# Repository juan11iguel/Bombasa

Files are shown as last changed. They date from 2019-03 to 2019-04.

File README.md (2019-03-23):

# Bombasa
En este proyecto intentamos implementar un arduino, con un driver para un motor DC y, haciendo uso de periféricos como una pantalla de 4 dígitos y 7 segmentos, así como de botones, interruptores, etc. Establecer dos modos de funcionamiento en un sistema cuyo objetivo es el impulso de reactivos químicos para mezcla de componentes (bomba PERISTÁLTICA*):

- El modo manual tiene como entrada la pulsación de dos botones, uno para aumentar y otro para disminuir, el rango de valores va de 0 a 20, y cada valor se corresponde con un valor de voltaje que se le introduce al motor y que hace propulsar un caudal determinado tras la calibración. El valor escogido, así como el voltaje que le corresponde y su caudal se muestran periódicamente en pantalla, así como en una tabla situada en la parte superior de la caja.
- El modo automático tiene dos opciones de funcionamiento, o bien toma la información de una tarjeta de entrada/salida (Labjack), que proporciona valores comprendidos entre 0 y 5V, el valor es leído por el Arduino en uno de sus puertos analógicos y codificado entre 0 y 1023, lo que a su vez ajusta al valor del PWM (0 - 255) y se introduce al driver. Otra opción es hacer uso de la comunicación por el puerto serie, que admite desde valores de la terminal serie incluída en el entorno de desarrollo de arduino, o bien a través de programas como Matlab (pendiente) o un sencillo programa desarrollado en Python (ya hecho y funcionando). 

Posteriormente, se intentará introducir un caudalímetro contador, que se introducirá en uno de los puertos digitales del Arduino, y se desarrollará un algoritmo para acondicionar esa información entrante y convertirla en un valor de caudal que se actualice cada pocos segundos, esta información se usará para cerrar un lazo de control, y haciendo uso de un controlador tipo PI controlar la bomba. También la idea es mandar la información instantánea del caudal como salida para poder realizar el registro de la información tomada.

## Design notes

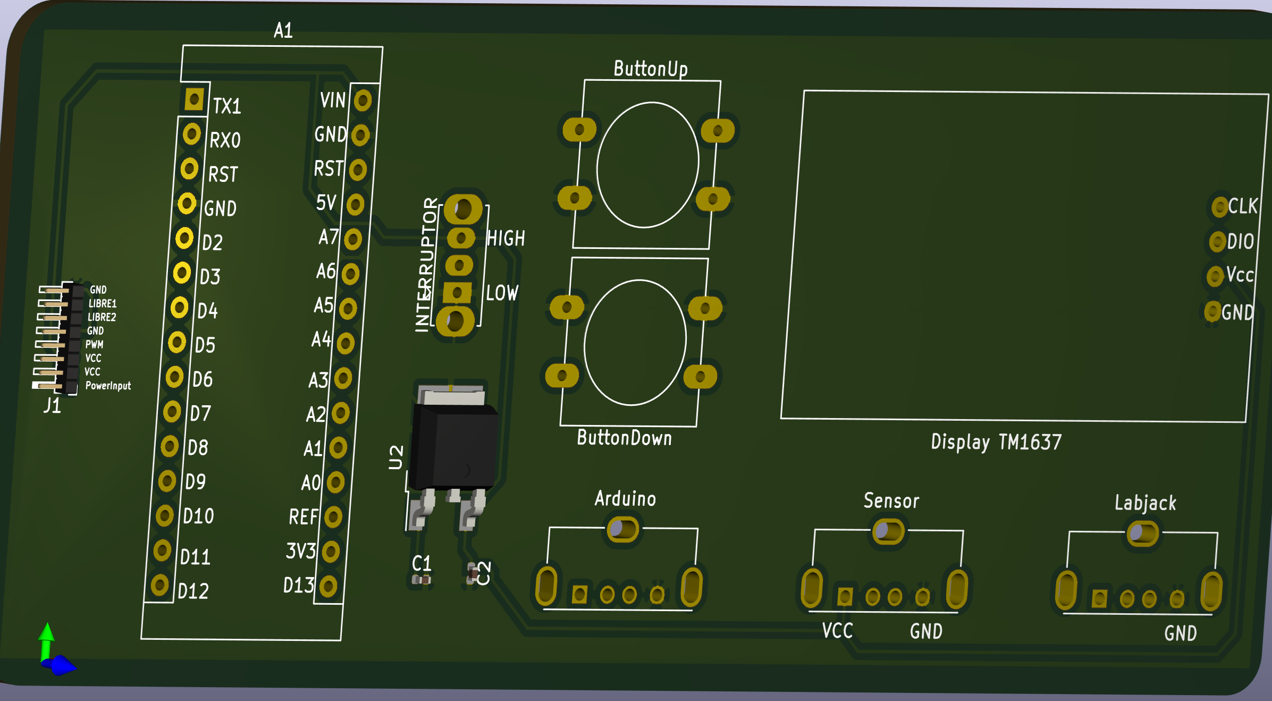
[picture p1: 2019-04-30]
ProyectoBombasa/Placa/ConNano/Sircuito3.png

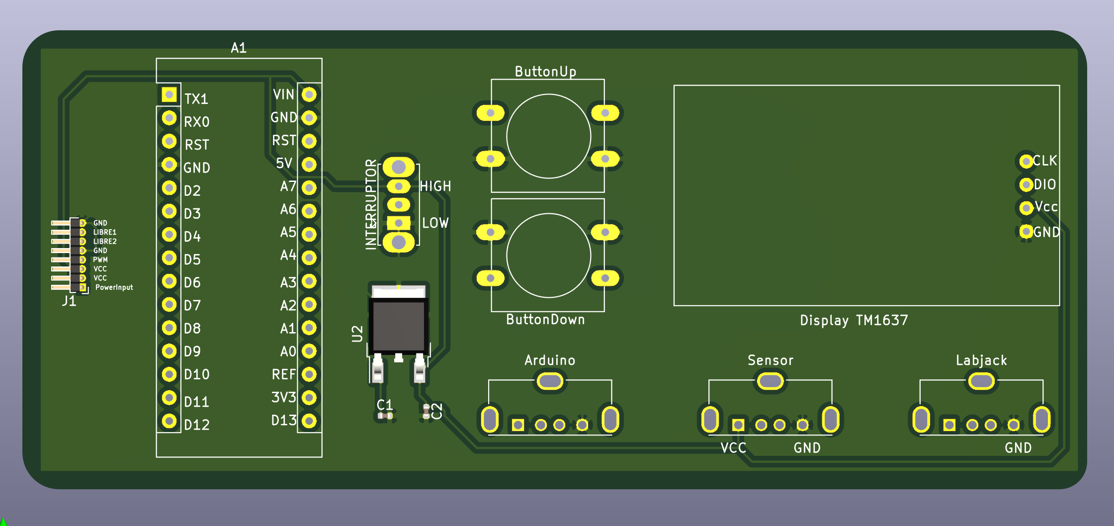
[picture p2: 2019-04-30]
ProyectoBombasa/Placa/ConNano/Sircuito.png

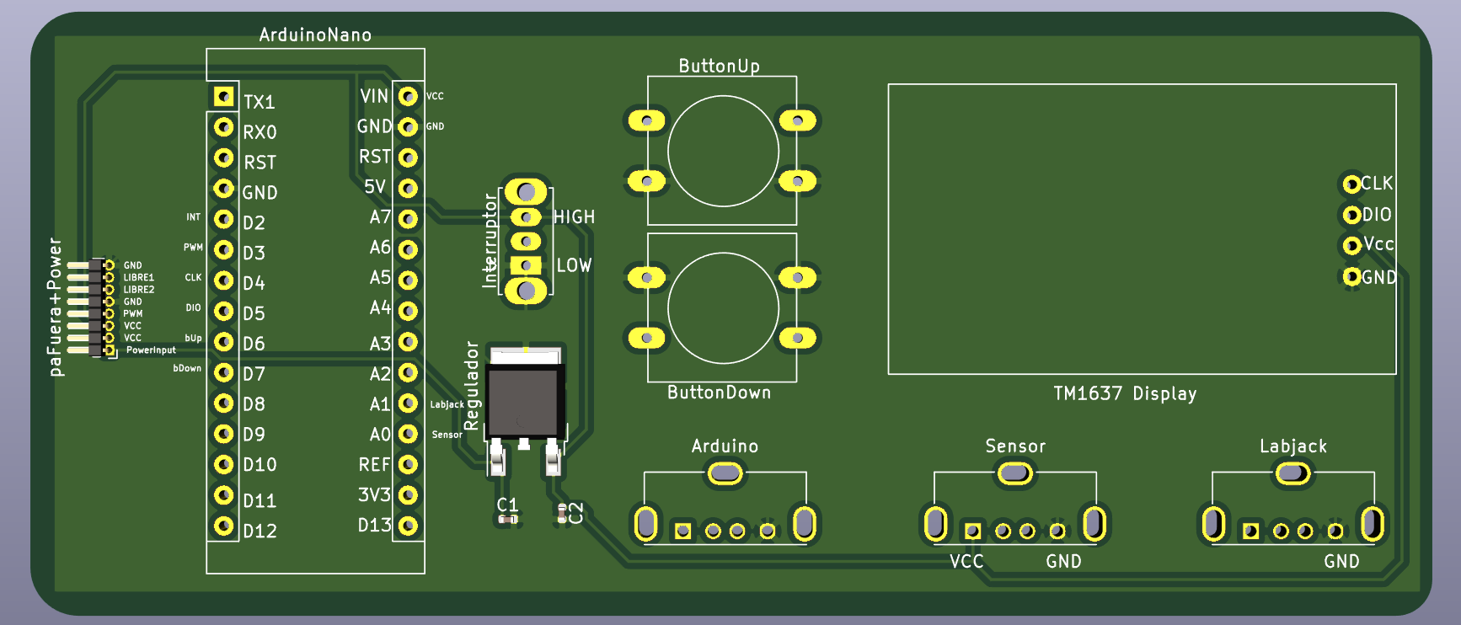
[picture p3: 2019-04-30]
ProyectoBombasa/Placa/ConNano/sircuitaso1.png

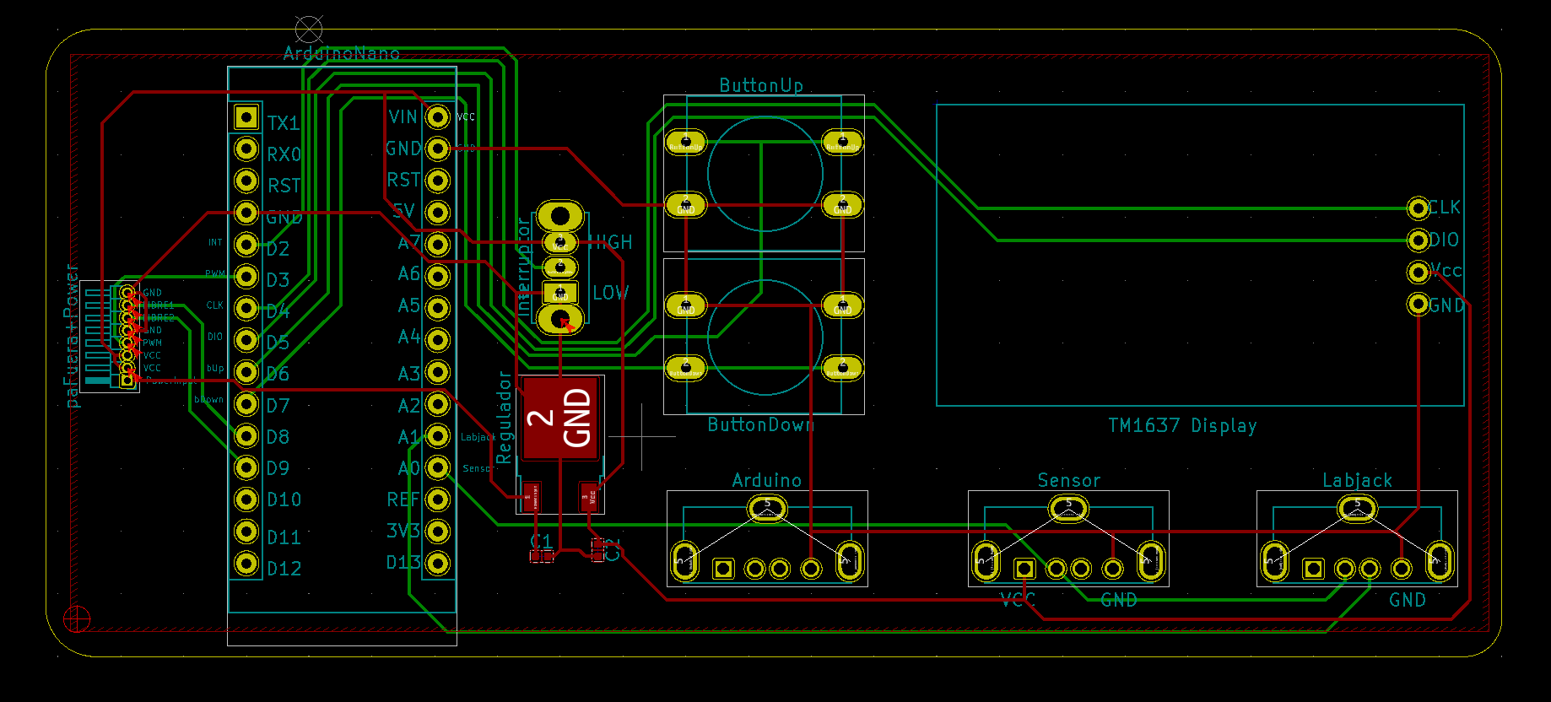
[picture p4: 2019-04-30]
ProyectoBombasa/Placa/ConNano/Sircuitaso.png

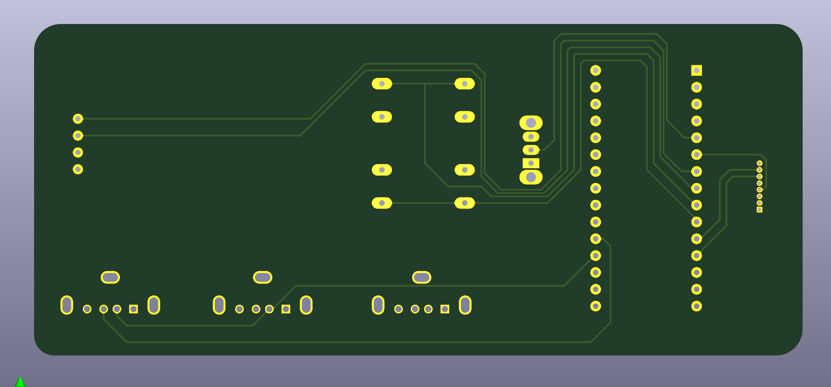
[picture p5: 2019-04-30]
ProyectoBombasa/Placa/ConNano/Sircuito2.png

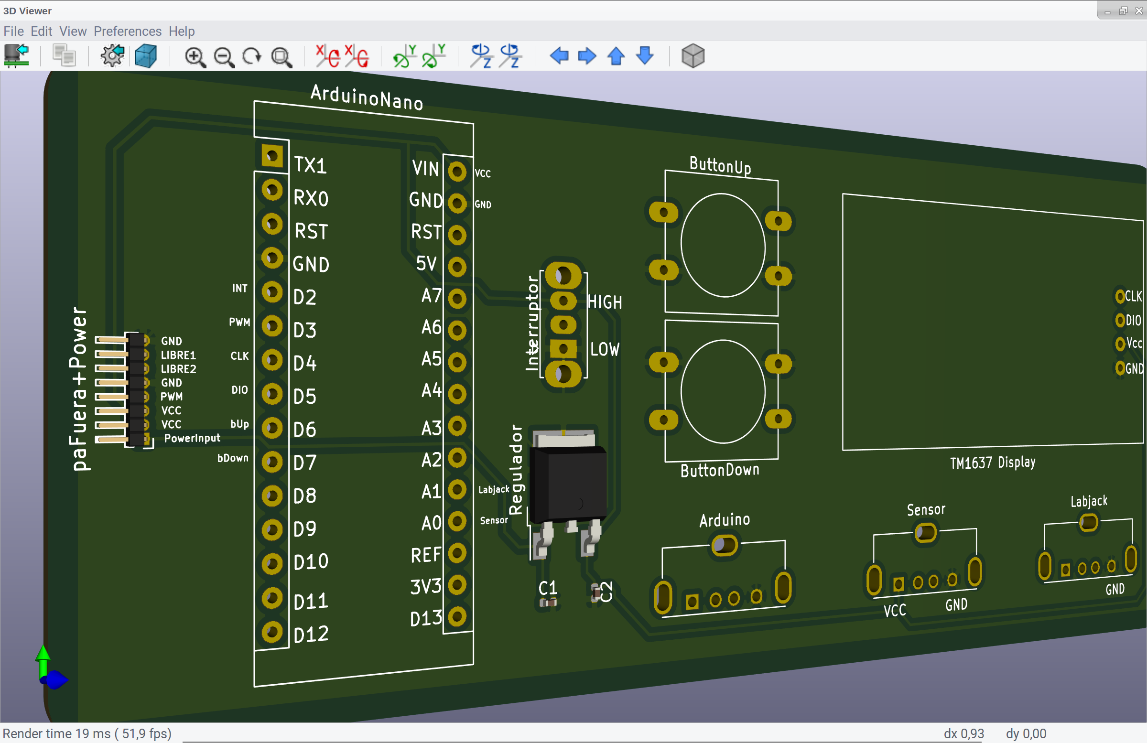
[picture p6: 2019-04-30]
ProyectoBombasa/Placa/ConNano/sircuitaso3.png

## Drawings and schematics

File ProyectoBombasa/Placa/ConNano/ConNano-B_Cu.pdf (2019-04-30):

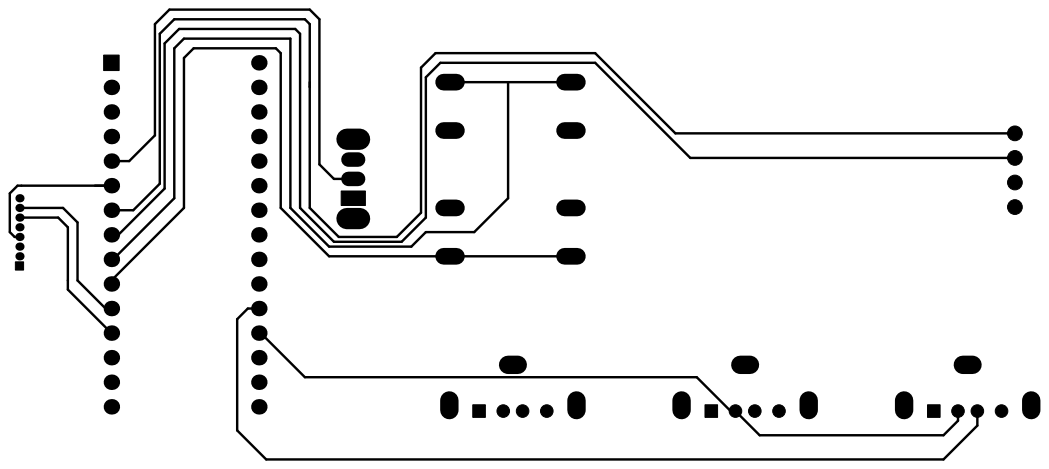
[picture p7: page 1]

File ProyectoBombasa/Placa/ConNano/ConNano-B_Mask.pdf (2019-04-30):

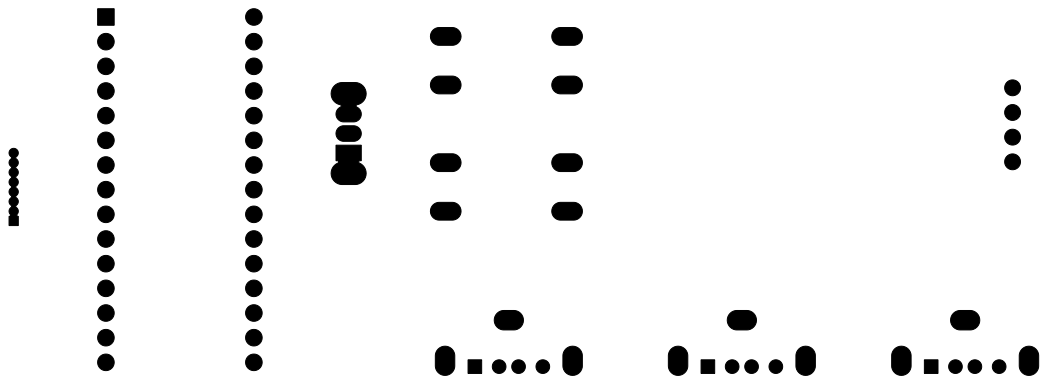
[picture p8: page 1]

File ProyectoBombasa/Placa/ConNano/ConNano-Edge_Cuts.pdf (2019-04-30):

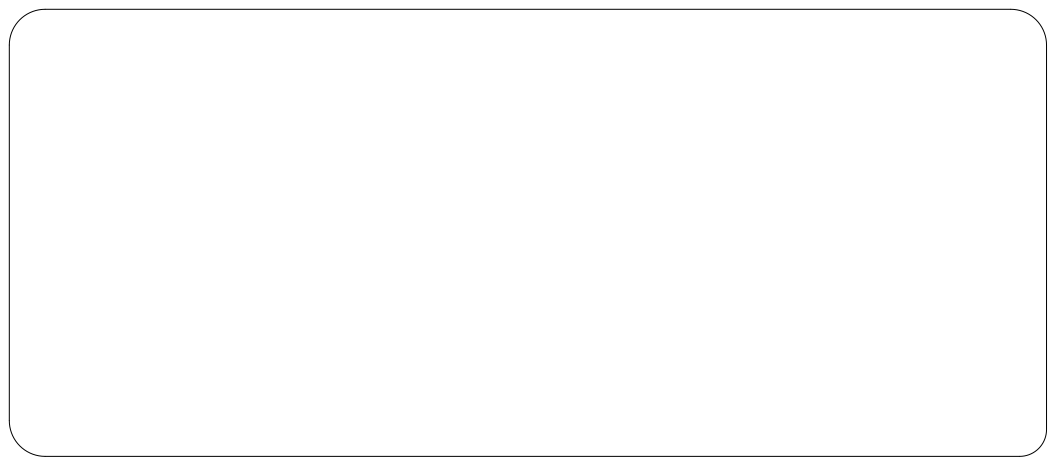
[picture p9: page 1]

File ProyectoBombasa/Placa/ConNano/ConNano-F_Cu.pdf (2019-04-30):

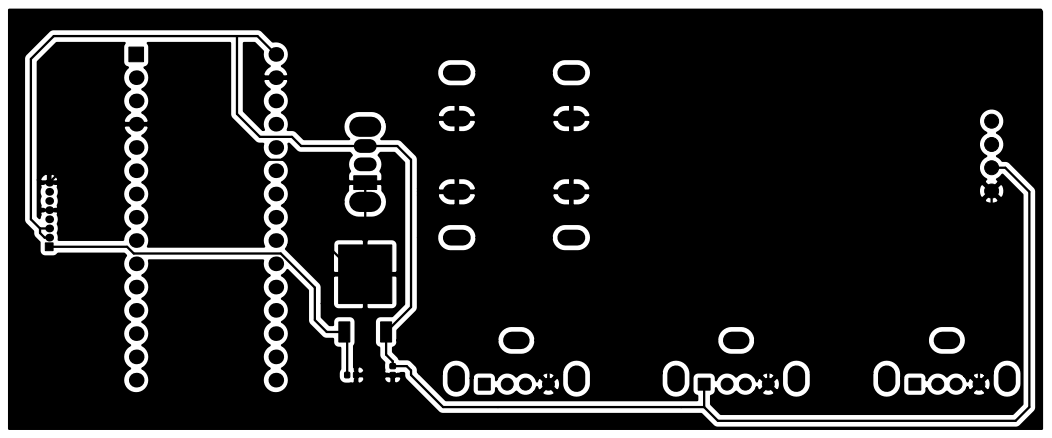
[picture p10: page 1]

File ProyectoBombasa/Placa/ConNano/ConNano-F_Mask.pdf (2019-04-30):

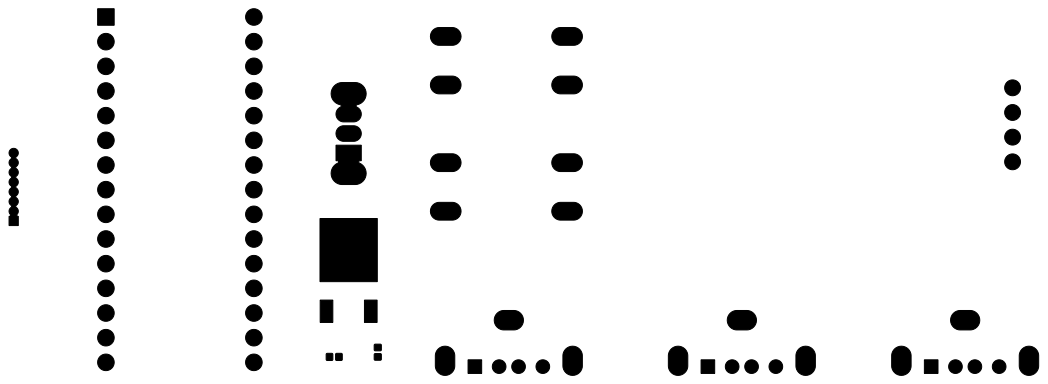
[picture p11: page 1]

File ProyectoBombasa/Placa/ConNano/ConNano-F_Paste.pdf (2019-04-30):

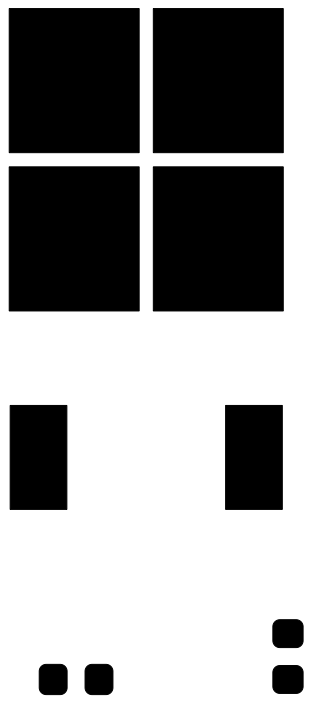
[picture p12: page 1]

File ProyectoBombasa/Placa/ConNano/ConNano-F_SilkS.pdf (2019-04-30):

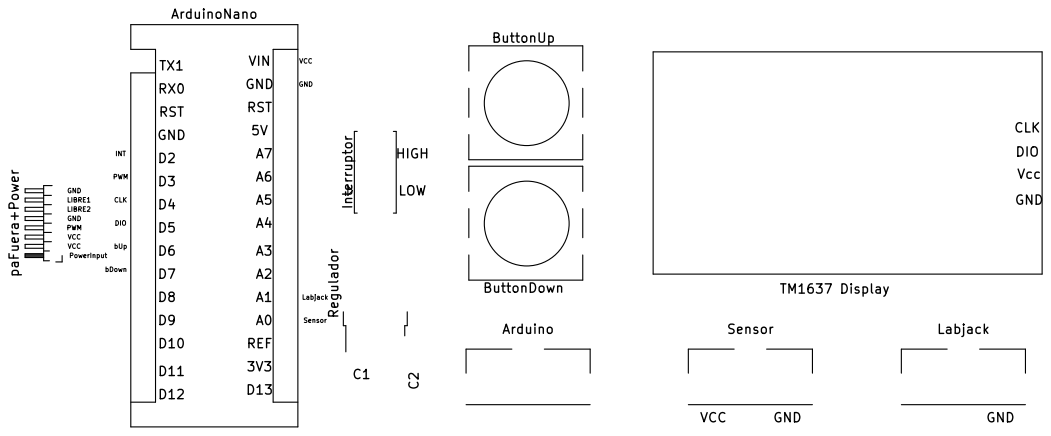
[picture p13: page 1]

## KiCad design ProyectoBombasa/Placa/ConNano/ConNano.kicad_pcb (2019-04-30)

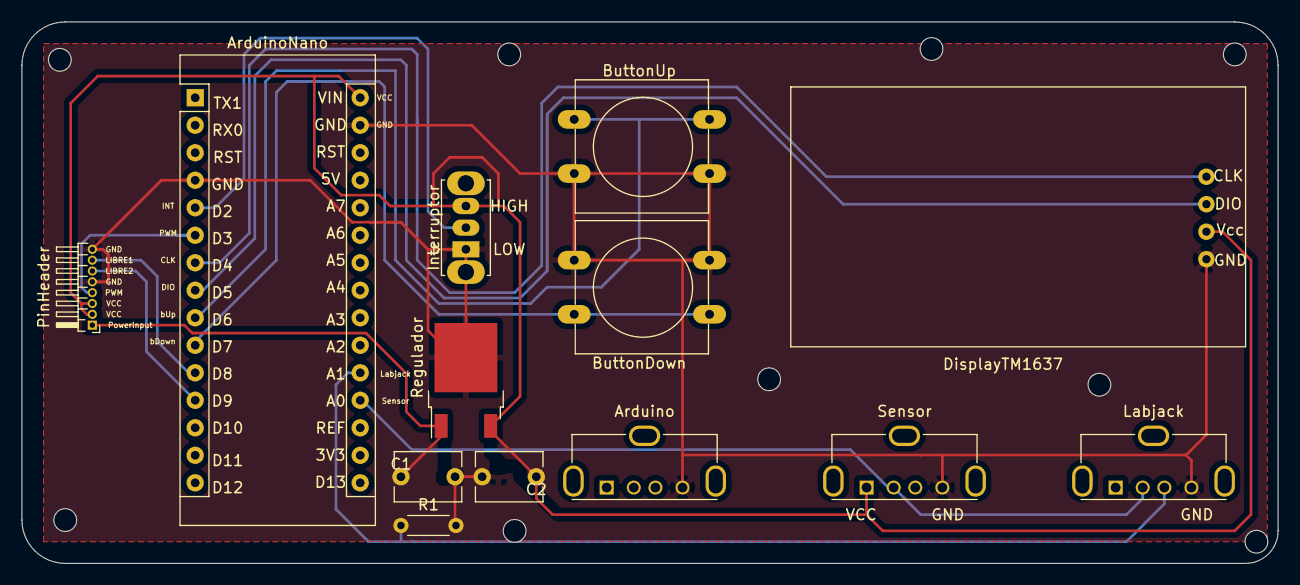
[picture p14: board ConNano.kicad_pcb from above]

Board: 2 copper layers, 116.0 x 50.0 mm, 13 parts (0 on the bottom side), 13 nets.

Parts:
Arduino: USB_A; USB_A_Molex_105057_Vertical
ArduinoNano: Arduino_Nano_v3.x; Arduino_Nano
ButtonDown: SW_Push; SW_PUSH-12mm
ButtonUp: SW_Push; SW_PUSH-12mm
C1: 0.33uF; C_Disc_D6.0mm_W4.4mm_P5.00mm
C2: 0.1uF; C_Disc_D6.0mm_W4.4mm_P5.00mm
DisplayTM1637: TM1637; TM1637Cool
Interruptor: SW_SPDT; SW_Slide_1P2T_CK_OS102011MS2Q
Labjack: USB_A; USB_A_Molex_105057_Vertical
PinHeader: Conn_01x08; PinHeader_1x08_P1.00mm_Horizontal
R1: 1k; R_Axial_DIN0204_L3.6mm_D1.6mm_P5.08mm_Horizontal
Regulador: L7805; TO-252-2
Sensor: USB_A; USB_A_Molex_105057_Vertical

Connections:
ButtonDown: ArduinoNano.10, ButtonDown.2
ButtonUp: ArduinoNano.9, ButtonUp.1
CLK: ArduinoNano.7, DisplayTM1637.1
DIO: ArduinoNano.8, DisplayTM1637.2
GND: Arduino.4, ArduinoNano.4, ButtonDown.1, ButtonUp.2, C1.2, C2.2, DisplayTM1637.4, Interruptor.1, Labjack.4, PinHeader.5, PinHeader.8, R1.2, Regulador.2, Sensor.4
Interruptor: ArduinoNano.5, Interruptor.2
LabjackSC: ArduinoNano.20, Labjack.3, R1.1
LabjackSensor: ArduinoNano.19, Labjack.2, Sensor.2
PWM: ArduinoNano.6, PinHeader.4
PowerInput: C1.1, PinHeader.1, Regulador.1
Vcc: ArduinoNano.30, C2.1, DisplayTM1637.3, Interruptor.3, PinHeader.2, PinHeader.3, Regulador.3, Sensor.1
porSiAca1: ArduinoNano.11, PinHeader.6
porSiAca2: ArduinoNano.12, PinHeader.7

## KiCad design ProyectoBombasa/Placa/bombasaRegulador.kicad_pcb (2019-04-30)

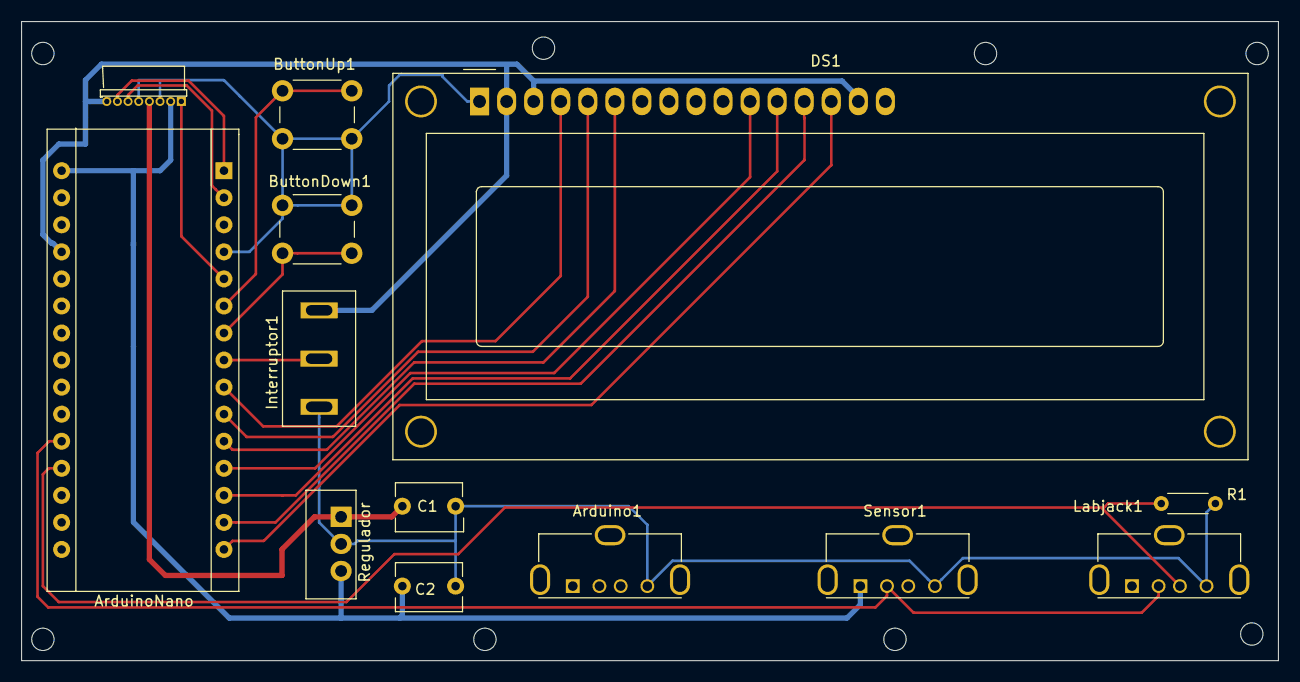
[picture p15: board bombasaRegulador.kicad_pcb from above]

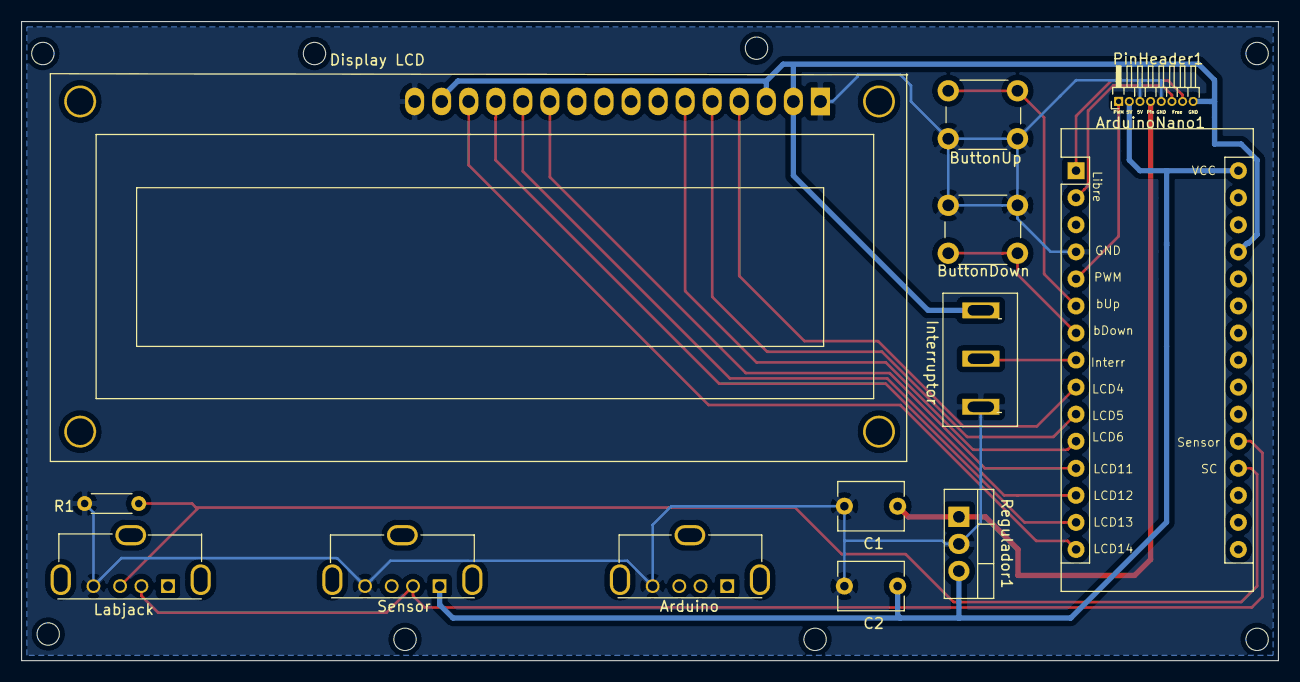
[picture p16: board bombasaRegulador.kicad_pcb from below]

Board: 2 copper layers, 118.0 x 60.0 mm, 13 parts (6 on the bottom side), 19 nets.

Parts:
Arduino1: USB_A; USB_A_Molex_105057_Vertical
ArduinoNano1: Arduino_Nano_v3.x; Arduino_Nano
ButtonDown1: SW_Push; SW_PUSH_6mm_H13mm
ButtonUp1: SW_Push; SW_PUSH_6mm_H13mm
C1: 0.33uF; C_Disc_D6.0mm_W4.4mm_P5.00mm
C2: 0.1uF; C_Disc_D6.0mm_W4.4mm_P5.00mm
DS1: WC1602A
Interruptor1: SW_SPDT; Interruptor
Labjack1: USB_A; USB_A_Molex_105057_Vertical
PinHeader1: Conn_01x08; PinHeader_1x08_P1.00mm_Horizontal
R1: 1k; R_Axial_DIN0204_L3.6mm_D1.6mm_P5.08mm_Horizontal
Regulador1: L7812; TO-220-3_Vertical
Sensor1: USB_A; USB_A_Molex_105057_Vertical

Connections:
5V: ArduinoNano1.27, DS1.2, DS1.3, DS1.15, Interruptor1.3, PinHeader1.5V
ButtonDown: ArduinoNano1.7, ButtonDown1.2
ButtonUp: ArduinoNano1.6, ButtonUp1.1
GND: Arduino1.4, ArduinoNano1.4, ButtonDown1.1, ButtonUp1.2, C1.2, C2.2, DS1.1, DS1.16, Interruptor1.1, Labjack1.4, PinHeader1.3, PinHeader1.5, R1.2, Regulador1.2, Sensor1.4
Interruptor: ArduinoNano1.8, Interruptor1.2
LCD4: ArduinoNano1.9, DS1.4
LCD5: ArduinoNano1.10, DS1.5
LCD6: ArduinoNano1.11, DS1.6
LCD11: ArduinoNano1.12, DS1.11
LCD12: ArduinoNano1.13, DS1.12
LCD13: ArduinoNano1.14, DS1.13
LCD14: ArduinoNano1.15, DS1.14
LabjackSC: ArduinoNano1.19, Labjack1.3, R1.1
LabjackSensor: ArduinoNano1.20, Labjack1.2, Sensor1.2
PWM: ArduinoNano1.5, PinHeader1.1
PowerInput: C1.1, PinHeader1.4, Regulador1.1
Vcc: ArduinoNano1.30, C2.1, PinHeader1.2, Regulador1.3, Sensor1.1
porSiAca1: ArduinoNano1.2, PinHeader1.6
porSiAca2: ArduinoNano1.1, PinHeader1.7

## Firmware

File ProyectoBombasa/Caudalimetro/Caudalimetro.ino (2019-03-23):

//  Programa para el control de la bomba en bucle cerrado

//  Inclusión de todas las librerías necesarias
#include <Arduino.h>
#include <TM1637Display.h>
#include <PID_v1.h>
/////////////////////////////////////////////

const int Vmax = 20;

// Se asocian los pines con su función
//  Motor
const int en1 = 3;      // PWM  Salida (0 - 255) bits -> (0 - 5) V
const int in1 = 7;      // Entrada lógica del driver para controlar el sentido de giro del motor
const int in2 = 4;      // Entrada lógica del driver para controlar el sentido de giro del motor

//  Elección
int ultimo_estado = 0;

//  Modo manual
const int botonUp = 13;     // Boton Subir (el de al lado de la pantalla)
const int botonDown = 12;   // Boton Bajar (el de al lado de la pantalla)
int estado_botonDown = 0;   // Estado actual del botón bajar
int buttonState = 0;        // Estado actual del botón subir
int lastButtonState = 0;    // Estado anterior del botón subir
int ultimo_estadoDown = 0;  // Estado anterior del botón bajar
int buttonPushCounter = 0;  // Contador de número de pulsaciones (subir suma, bajar resta)

//  Modo automático
const int Labjack = A4;     // Entrada del Labjack para controlar el motor (0-1023) bits -> (0 - 5) V


//Pantalla 7 segmentos 4 dígitos/////////////////////////////////
/////////////////////////////////////////////////////////////////
#define CLK 11                                              /////
#define DIO 10                                              /////
                                                            /////
const uint8_t SEG_MAN[] = {                                 /////
  SEG_E | SEG_F | SEG_A | SEG_B | SEG_C,                    // M
  SEG_F | SEG_A | SEG_B | SEG_C | SEG_E,                    // 
  SEG_C | SEG_E | SEG_G | SEG_F | SEG_A | SEG_B,            // A
  SEG_F | SEG_A | SEG_E | SEG_F | SEG_B | SEG_C,            // N
};                                                          /////
                                                            /////
const uint8_t SEG_AUTO[] = {                                /////
  SEG_C | SEG_E | SEG_G | SEG_F | SEG_A | SEG_B,            // A
  SEG_E | SEG_F | SEG_D | SEG_B | SEG_C,                    // U
  SEG_A | SEG_B | SEG_C,                                    // T
  SEG_A | SEG_E | SEG_F | SEG_B | SEG_C | SEG_D,            // O
};                                                          /////
                                                            /////
const uint8_t SEG_OCHO[] = {                                /////
  SEG_A | SEG_B | SEG_C | SEG_D | SEG_E | SEG_F | SEG_G,    // 8
  SEG_A | SEG_B | SEG_C | SEG_D | SEG_E | SEG_F | SEG_G,    // 8
  SEG_A | SEG_B | SEG_C | SEG_D | SEG_E | SEG_F | SEG_G,    // 8
  SEG_A | SEG_B | SEG_C | SEG_D | SEG_E | SEG_F | SEG_G,    // 8
};                                                          /////
                                                            /////
TM1637Display display(CLK, DIO);                            /////
/////////////////////////////////////////////////////////////////

//  Interruptor MANUAL - AUTOMÁTICO
const int interruptor = 2;
int estado_interruptor = 0;


//  Caudalímetro Contador
int caudalimetro = 8;

//  Variables para la función leer caudal
int contador = 0;
int ultimo_estadoo = 0;
int estado;
int tiempo;
int ultimo_tiempo = 0;
float f;
int conteo = 0;
int variacion;


//  Lectura Voltaje
int lectura_Voltaje = A5;
float V;


//  Sólo se ejecuta una vez, establece la configuración inicial
void setup() {
  // Asignación de entradas y salidas
  Serial.begin(9600);
  pinMode(interruptor, INPUT);
  pinMode(botonUp, INPUT);
  pinMode(botonDown, INPUT);
  pinMode(caudalimetro, INPUT);

  pinMode(en1, OUTPUT);
  pinMode(in1, OUTPUT);
  pinMode(in2, OUTPUT);


  display.clear(); //Limpia la pantalla
  display.setBrightness(0x0f); 
  display.setSegments(SEG_OCHO);
  delay(1);
  
  if(digitalRead(interruptor == 1)){    //Para que si el sistema se inicia en modo AUTO
     ultimo_estado = 1;                 //el ultimo_estado lo refleje y represente el 8888.
  }
}


// Se ejecuta continuamente, se incluyen aquí todas las tareas a realizar
void loop() {

  // ELECCIÓN MANUAL - AUTOMÁTICO
  eleccion();
  //f=leerCaudal();
  
  leerVoltaje();
  
}




//  Procedimiento que lee el estado del interruptor y lleva el programa al modo AUTO o MANUAL
void eleccion() {

  
  estado_interruptor = digitalRead(interruptor);

  if (estado_interruptor == HIGH) {
    //Entonces el interruptor está en modo AUTOMÁTICO
    if(ultimo_estado != estado_interruptor){
      display.setSegments(SEG_AUTO);
    }                                                             
    automatico();
    
  } else {
    //Entonces el interruptor está en modo MANUAL
    manual();
    if(ultimo_estado != estado_interruptor){
      display.setSegments(SEG_MAN);
    }                          
  }
  
  ultimo_estado = estado_interruptor;
}




// Subprograma que contiene el modo MANUAL
void manual() {
  int value = 0;
  
    // read the pushbutton input pin:
  buttonState = digitalRead(botonUp);
  // compare the buttonState to its previous state
  if (buttonState != lastButtonState) {
    // if the state has changed, increment the counter
    if (buttonState == HIGH && buttonPushCounter < Vmax) {
      // if the current state is HIGH then the button went from off to on:
      buttonPushCounter++;
      Serial.println("on");
      Serial.print("number of button pushes: ");
      Serial.println(buttonPushCounter);
      
      display.setBrightness(0x0f); 
      display.showNumberDec(buttonPushCounter,false);
      
    } 
    // Delay a little bit to avoid bouncing
    delay(50);
  }
  // save the current state as the last state, for next time through the loop
  lastButtonState = buttonState;


  estado_botonDown = digitalRead(botonDown);

  // compare the buttonState to its previous state
  if (estado_botonDown != ultimo_estadoDown) {
    // if the state has changed, increment the counter
    if (estado_botonDown == HIGH && buttonPushCounter > 0) {
      buttonPushCounter--;
      Serial.println("off");
      Serial.print("number of button pushes: ");
      Serial.println(buttonPushCounter);
      display.setBrightness(0x0f);
      display.showNumberDec(buttonPushCounter,false); 
    } 
    delay(50);    
  }
  // save the current state as the last state, for next time through the loop
  ultimo_estadoDown = estado_botonDown;


    
    MoverMotor(buttonPushCounter);
}




//  Subprograma que contiene el modo automático
void automatico() {
  float valor = 0;  // valor de salida Analógica para motor1. Inicializar
  int value = 0;
  int lastValue = 0;

  
  
  value = analogRead(Labjack);
  if (analogRead(Labjack) > 0.1 && value != lastValue) {
    //Se toman las referencias a partir del Labjack
    valor = analogRead(Labjack); //0-5V
    Serial.println("Labjack funsionando papi");
    Serial.println();
    Serial.print("El valor introducido es: ");   
    Serial.println(valor);
    
    MoverMotor(valor);

  } else { 
  
    if (Serial.available() > 0) {
      Serial.println("Introduzca un valor de 0 - 1024 (resolución de la salida analog) ");
      String str = Serial.readStringUntil('\n'); //lectura de la entrada de varios dígitos
      float valor = str.toFloat();

      if (valor>=0 && valor <=100){

        //Mover_motor
        MostrarPantalla(valor);
        MoverMotorSerial(valor);


    
        Serial.println();
        Serial.print("El valor introducido es: ");   
    
        Serial.println(valor);
      }
    }
  }

}



//  Subprograma para la representación en pantalla de números reales con hasta dos decimales
void MostrarPantalla(float valor){

  int entera = 0;
  int decimal = 0;

  //Ajuste de número real para separarlo en dos enteros de parte real e imaginaria
  entera = (int)(valor);
  decimal = round(100 * (valor - entera)); 

  //Representación en pantalla del número real
    display.clear(); //Limpia la pantalla
    display.setBrightness(0x0f); 
    display.showNumberDecEx(entera,(0x80 >> 1),false,2,0); 
    display.showNumberDecEx(decimal,(0x80 >> 1),false,2,2); 
}


//  Subprograma para el movimiento del motor en modo manual
void MoverMotor(float valor){

  digitalWrite(in1, HIGH);
  digitalWrite(in2, LOW);
  if(valor == 0){
    analogWrite(en1,valor);
  }else{
    valor = map(valor, 0, 27.4, 4.4, 22);
    valor = map(valor, 4.4, 25.4, 37.4, 255);
    analogWrite(en1,valor);
  }

  
//  Subprograma para el movimiento del motor en modo automático, por el puerto serie
}

void MoverMotorSerial(float valor){

  digitalWrite(in1, HIGH);
  digitalWrite(in2, LOW);

    valor = map(valor, 0, 100, 0, 28);
    valor = map(valor, 0, 28, 0, 255);
    analogWrite(en1,valor);
  
  
}


//  Función para realizar la lectura del caudalímetro contador y asociarla al caudal correspondiente
float leerCaudal(){
  float frecuencia;
  

  tiempo=millis();

  estado=digitalRead(caudalimetro);

  
  if(estado == HIGH && estado != ultimo_estadoo){
    Serial.println("Hola");
    
    variacion = tiempo - ultimo_tiempo;
    frecuencia = 1/variacion;

    Serial.print("freq:");
    Serial.println(frecuencia);
    Serial.print("estado: ");
    Serial.println(estado);
    Serial.print("contador: ");
    Serial.println(contador);
    contador++;

  }
  ultimo_estadoo = estado;
  ultimo_tiempo = tiempo;
  
  
  return frecuencia;
  
}

//  Subprograma que lee el voltaje enviado el motor, a través del divisor de tensión para adaptarla
//  al rango de entrada del puerto analógico del arduino

void leerVoltaje(){
int voltaje[5];

  tiempo=millis();

  if(tiempo - ultimo_tiempo > 10){

      V=analogRead(A5);

      if( V != 0 && V != 1023){
       
      }

  if(tiempo - ultimo_tiempo > 1000){
    
  }
      
      if( V != 0 && V != 1023){
        Serial.print("Voltaje enviado al motor: ");
        Serial.println(V);
      
      }
      
//(V <800 || V> 850)&&
      ultimo_tiempo = tiempo;
  }

}

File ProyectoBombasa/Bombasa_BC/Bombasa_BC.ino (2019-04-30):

//  Programa para el control de la bomba en bucle cerrado

//  Inclusión de todas las librerías necesarias
#include <Arduino.h>
#include <math.h>
#include <TM1637Display.h>
#include <PID_v1.h>
////////////////////////////////////////////////////////////////////////////////////////////////////////////////////////
////////////////////////////////////////////////////////////////////////////////////////////////////////////////////////

//Definición e inicialización de variables
const int Vmax = 24;
const int QMAX = 60;

// Se asocian los pines con su función
//  Motor
void MoverMotor(float valor);
const int en1 = 3;      // PWM  Salida (0 - 255) bits -> (0 - 5) V
const int in1 = 7;      // Entrada lógica del driver para controlar el sentido de giro del motor
const int in2 = 4;      // Entrada lógica del driver para controlar el sentido de giro del motor

//  Elección
int ultimo_estado = 0;

//  Modo manual
const int botonUp = 4;     // Boton Subir (el de al lado de la pantalla)
const int botonDown = 5;   // Boton Bajar (el de al lado de la pantalla)
int estado_botonDown = 0;   // Estado actual del botón bajar
int buttonState = 0;        // Estado actual del botón subir
int lastButtonState = 0;    // Estado anterior del botón subir
int ultimo_estadoDown = 0;  // Estado anterior del botón bajar
int buttonPushCounter = 0;  // Contador de número de pulsaciones (subir suma, bajar resta)

//  Modo automático
const int Labjack = A4;     // Entrada del Labjack para controlar el motor (0-1023) bits -> (0 - 5) V

//  Interruptor MANUAL - AUTOMÁTICO
const int interruptor = 2;
int estado_interruptor = 0;

//  Caudalímetro
double Qmedio = 0;
double leerCaudal();
int Q;            //Variable que almacena la lectura instantánea del voltaje
int nlecturas = 0; //Almacena el número de lecturas (100 lecturas)
int caudal[20]; //Almacena el valor de V para las nlecturas


// Interpreteción del voltaje que da el caudalímetro en caudal
double calibracionCaudalimetro(double x);

// Ajuste polinomial de los parámetros del sistema en base al punto de operación
//ganancia
double ganancia(double x);
//constante de tiempo
double cteTiempo(double x);

void eleccion();

//Parámetros de la planta
double k = 0;
double tau = 0;

//  Controlador
double Input;
double Output;
double Setpoint;

//Parámetros del controlador de caudal.  PARALELO
double Kp_Q;
double Ki_Q;

int ultimo_tiempo = 0;
int tiempo;

PID ControlCaudal(&Input, &Output, &Setpoint, Kp_Q, Ki_Q, 0, DIRECT);

//  Variables auxiliares que se comparten en distintos subprogramas
int i;
float suma;


void pantallaOscilante(double Input, double Output);
//Pantalla 7 segmentos 4 dígitos/////////////////////////////////
/////////////////////////////////////////////////////////////////
#define CLK 7                                              /////
#define DIO 6
double ultiempodisplay = 0;
double tiempodisplay = 0;/////
/////
const uint8_t SEG_MAN[] = {                                 /////
  SEG_E | SEG_F | SEG_A | SEG_B | SEG_C,                    // M
  SEG_F | SEG_A | SEG_B | SEG_C | SEG_E,                    //
  SEG_C | SEG_E | SEG_G | SEG_F | SEG_A | SEG_B,            // A
  SEG_F | SEG_A | SEG_E | SEG_F | SEG_B | SEG_C,            // N
};                                                          /////
/////
const uint8_t SEG_AUTO[] = {                                /////
  SEG_C | SEG_E | SEG_G | SEG_F | SEG_A | SEG_B,            // A
  SEG_E | SEG_F | SEG_D | SEG_B | SEG_C,                    // U
  SEG_A | SEG_B | SEG_C,                                    // T
  SEG_A | SEG_E | SEG_F | SEG_B | SEG_C | SEG_D,            // O
};                                                          /////
/////
const uint8_t SEG_OCHO[] = {                                /////
  SEG_A | SEG_B | SEG_C | SEG_D | SEG_E | SEG_F | SEG_G,    // 8
  SEG_A | SEG_B | SEG_C | SEG_D | SEG_E | SEG_F | SEG_G,    // 8
  SEG_A | SEG_B | SEG_C | SEG_D | SEG_E | SEG_F | SEG_G,    // 8
  SEG_A | SEG_B | SEG_C | SEG_D | SEG_E | SEG_F | SEG_G,    // 8
};                                                          /////
/////
TM1637Display display(CLK, DIO);                            /////
/////////////////////////////////////////////////////////////////


////////////////////////////////////////////////////////////////////////////////////////////////////////////////////////
////////////////////////////////////////////////////////////////////////////////////////////////////////////////////////


//Programas y subprogramas
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

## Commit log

2019-03-18 Add files via upload
    Librerías necesarias para poder compilar y subir el programa Bombasa.ino
2019-03-18 Carpeta contenedora del proyecto
    [valores.csv]
2019-03-19 Última actualisasió
    Añade la característica de que muestre en pantalla MAN o AUTO cuando se conmuta de modo.
2019-03-19 Versión Base sobre la que trabajar
2019-03-19 Arreglado problema display
    Ahora ya muestra correctamente todos los decimales, he añadido round() a cuando sacaba la parte decimal como entera.
2019-03-20 Ultima version
    Actualizado el sketch caudalimetro para intentar implementar leer la frecuencia con el contador, pero principalmente para intentar leer el voltaje que se le introduce al motor.
2019-03-22 Para probar a representar la medida en tiempo real
2019-03-22 Código Matlab
    Código Matlab para representación y tratamiento de datos.
2019-03-23 Última versión de Caudalimetro
    Añadidos algunos comentarios y limpiado un poco el código.
    Tareas pendientes:
    - Hacer subprograma caudalimetro que devuelva el caudal cada x tiempo como la media de los valores tomados en ese intervalo.
    - Añadir a leerVoltaje para que devuelva cada x tiempo la media de los valores leídos en ese intervalo.
    - Incluir el controlador para el control automático del voltaje enviado para seguir la consigna de entrada.
    - Sacar modelos para diseñar controladores.
    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
2019-03-24 Cambio de algunos nombres para organizar mejor.
2019-03-31 Registra la lectura del sensor en un archivo
